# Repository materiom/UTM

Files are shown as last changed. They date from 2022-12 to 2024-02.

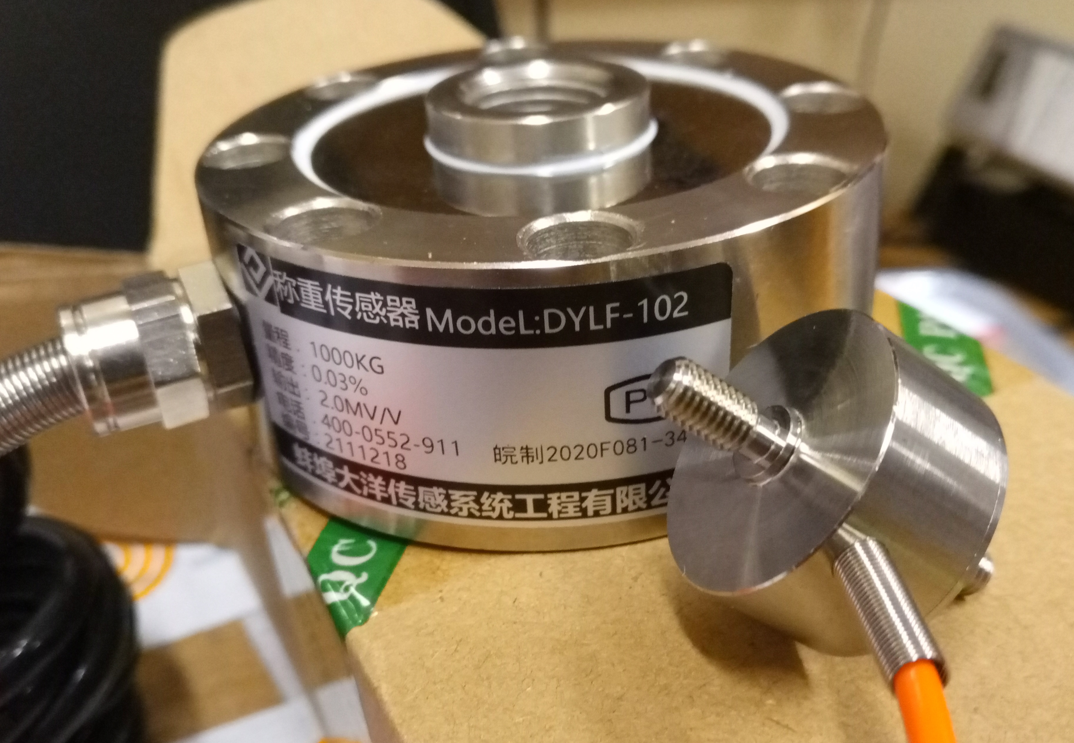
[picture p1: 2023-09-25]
Docs/Doc images/Mechanical - miscellaneous/Load cell photos/Load cell photo.jpg

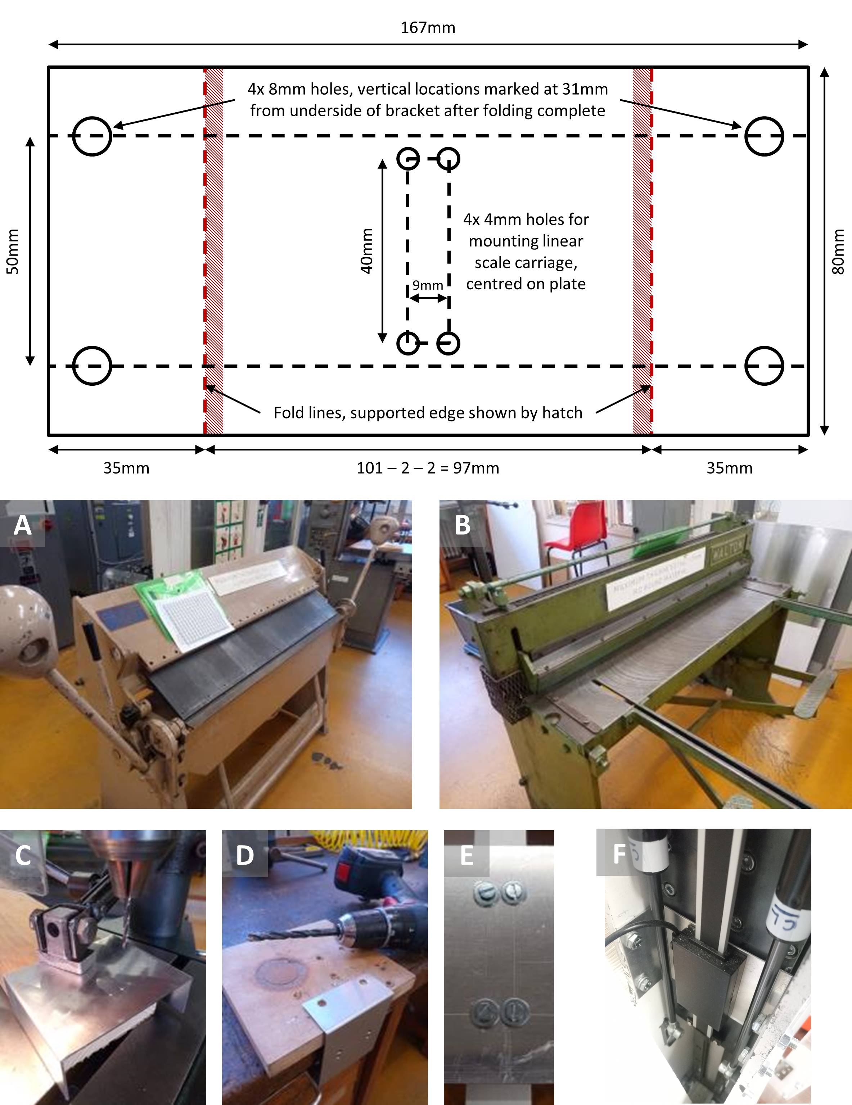
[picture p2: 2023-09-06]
Docs/Doc images/Mechanical - miscellaneous/Linear scale bracket/Linear scale bracket tiled.jpg

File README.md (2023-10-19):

# UTM
Documentation the Materiom Universal Testing Machine

[<b>Read the Documentation - Wiki</span></b>](../../wiki) 

## Introduction

Why do I want to build a UTM?

What solutions are out there (Link to Dave and Richards combined document)

Why another UTM? Why ours?

What problem(s) does it solve?

What is the overall aim for the UTM project

Describe the components
  - Control System / Software - Schematic of how the components all work together
  - User Interface (GUI) - ...
  - Integration with Materiom's database (if this matches with Materiom's goals?)

## Documentation

Description of what is in the documentation and an overview of the structure - add links to the docs here
  
  - Bill of Materials - Items, Quantities, Suggested suppliers, (estimated costs?)
  - CAD files - DXF files, FreeCAD assemblies, CAD library

  - Software use instructions 

## Contribution Guidelines

How can the community contribute to this project?

How can they feedback problems/improvements to make the UTM an ever-improving machine.

Folders in the repo for expansion module information - environmental chamber, heat chamber ideas etc.

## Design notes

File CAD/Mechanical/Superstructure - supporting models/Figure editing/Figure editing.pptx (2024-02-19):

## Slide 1

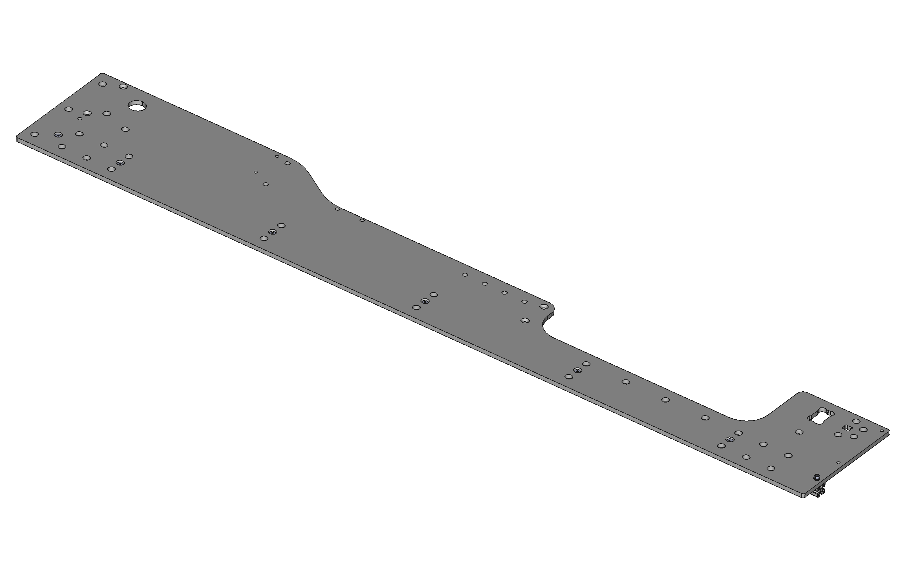
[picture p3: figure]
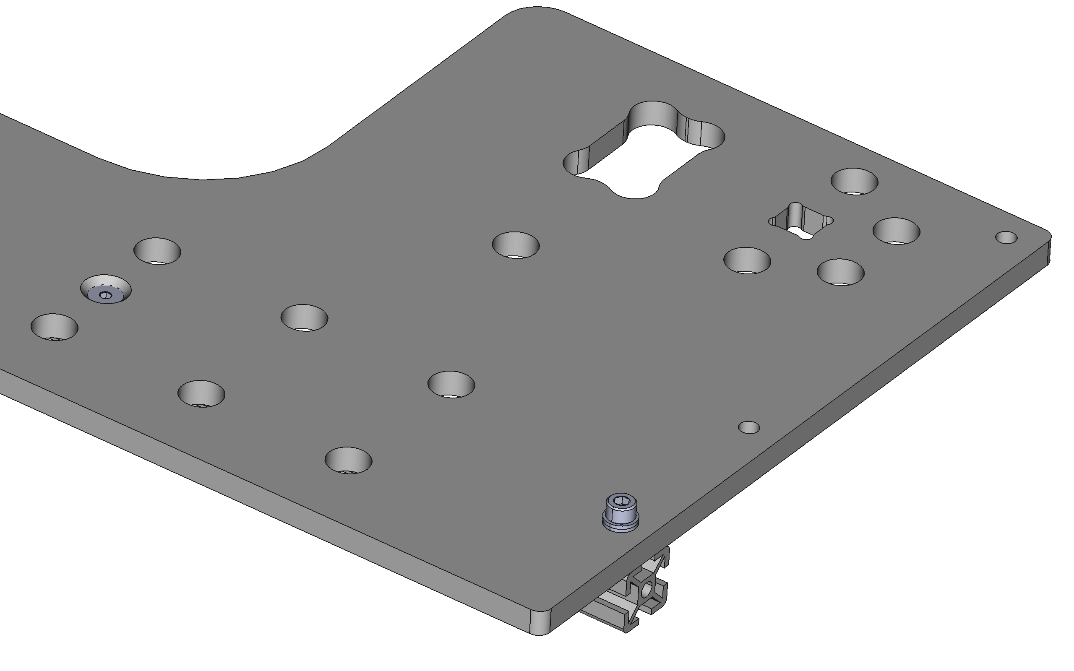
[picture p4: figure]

Rail end aligned with plate end

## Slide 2

Mount centring ring with 2x M4x16mm countersunk head screws

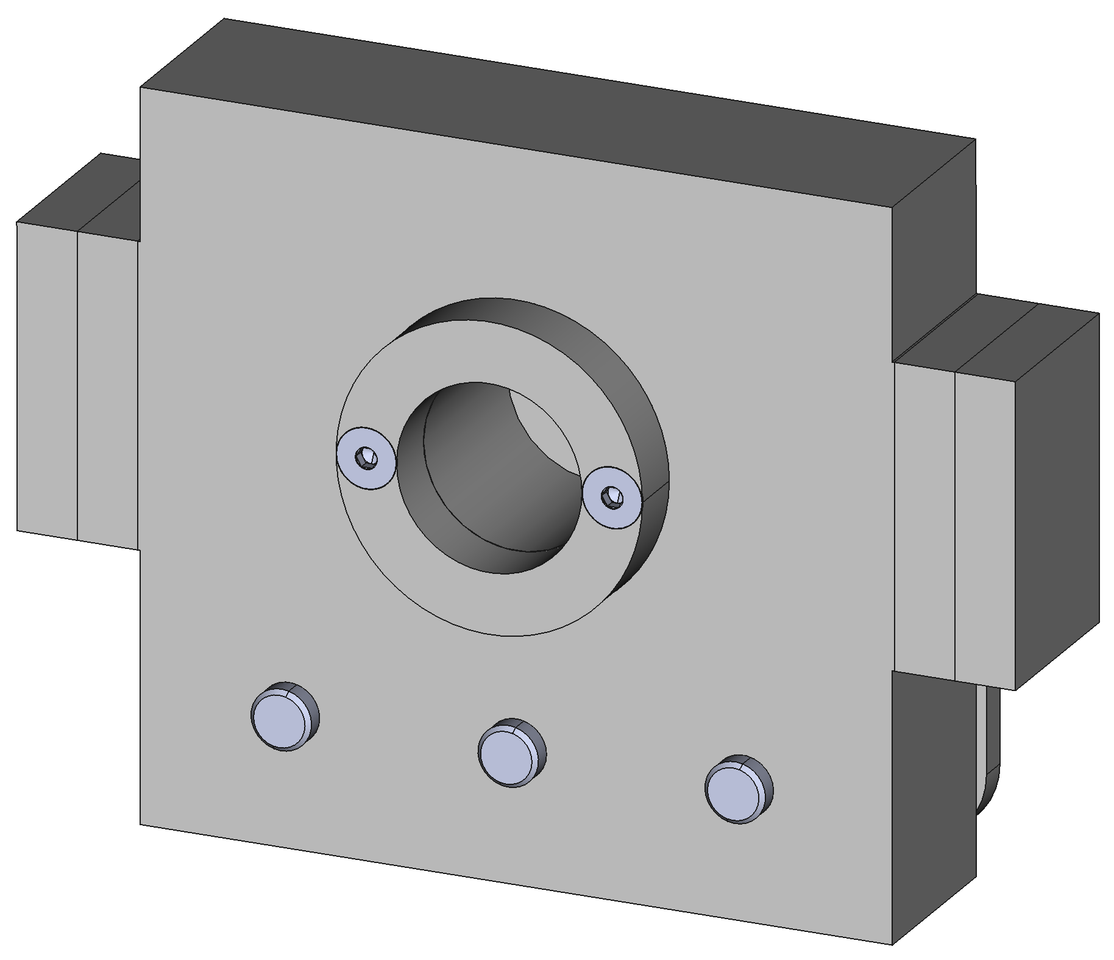
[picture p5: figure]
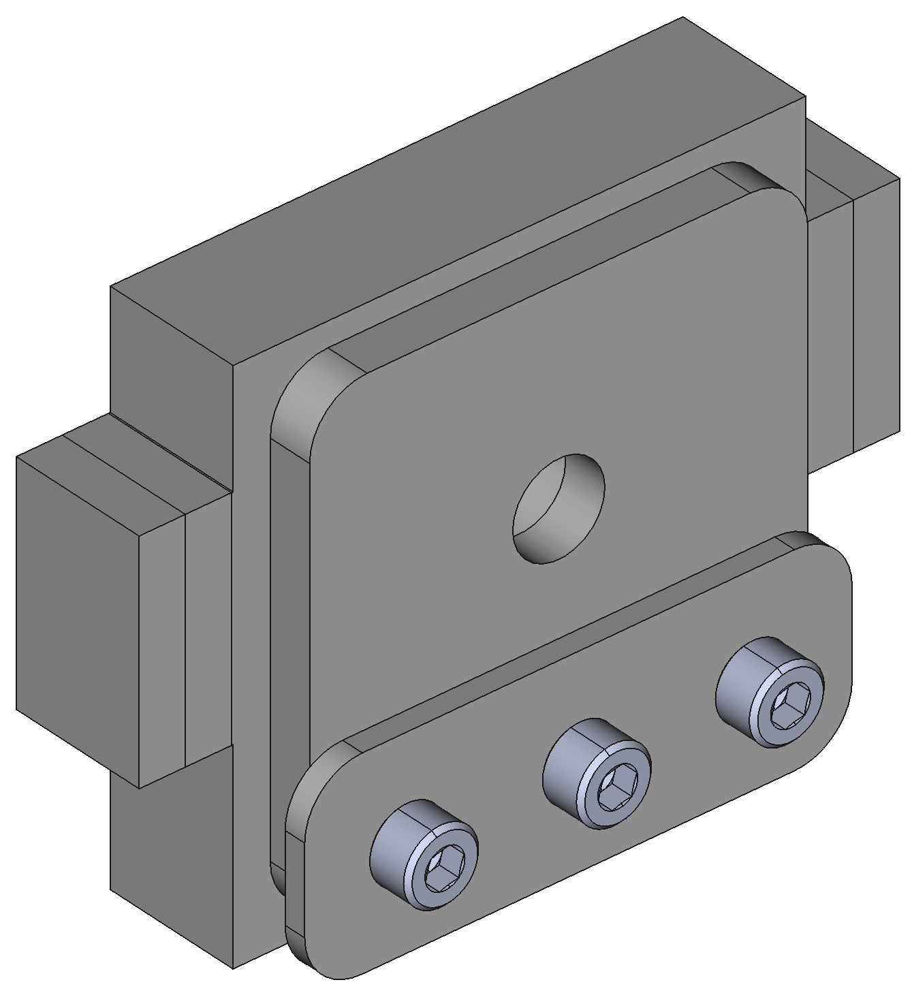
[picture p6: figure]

Mount alignment and associated cap plate with 3x M8x40mm cap head screws

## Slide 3

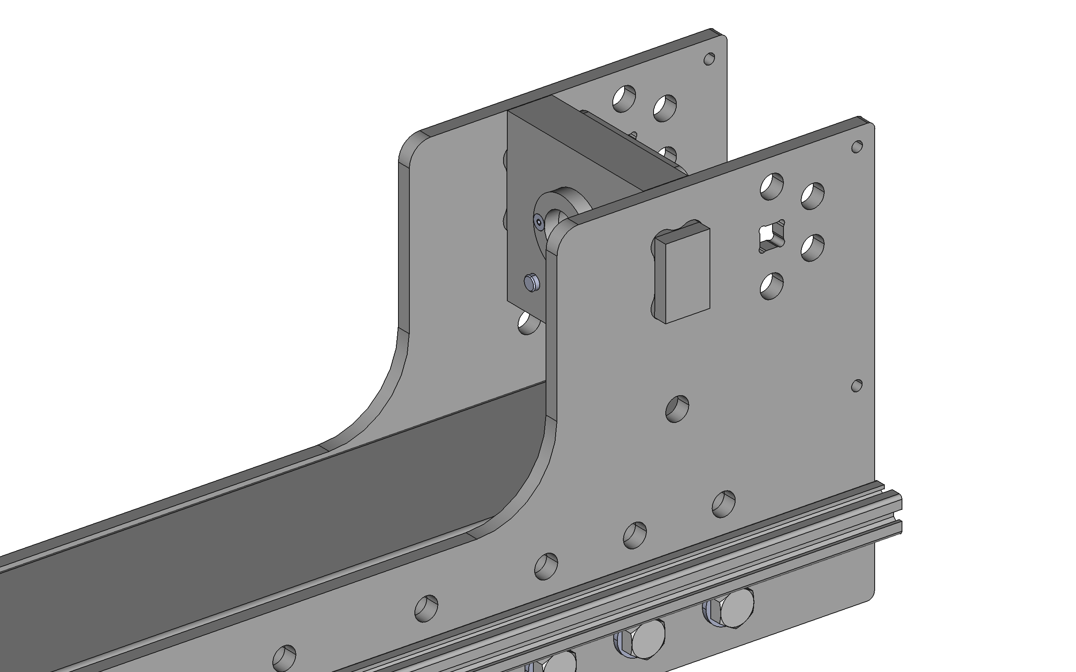
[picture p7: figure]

2. Cut and insert steel shims as necessary to correct alignment of tabbed end plate

1. Check perpendicularity of inside edge of tabbed end plate to instrument side panels

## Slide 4

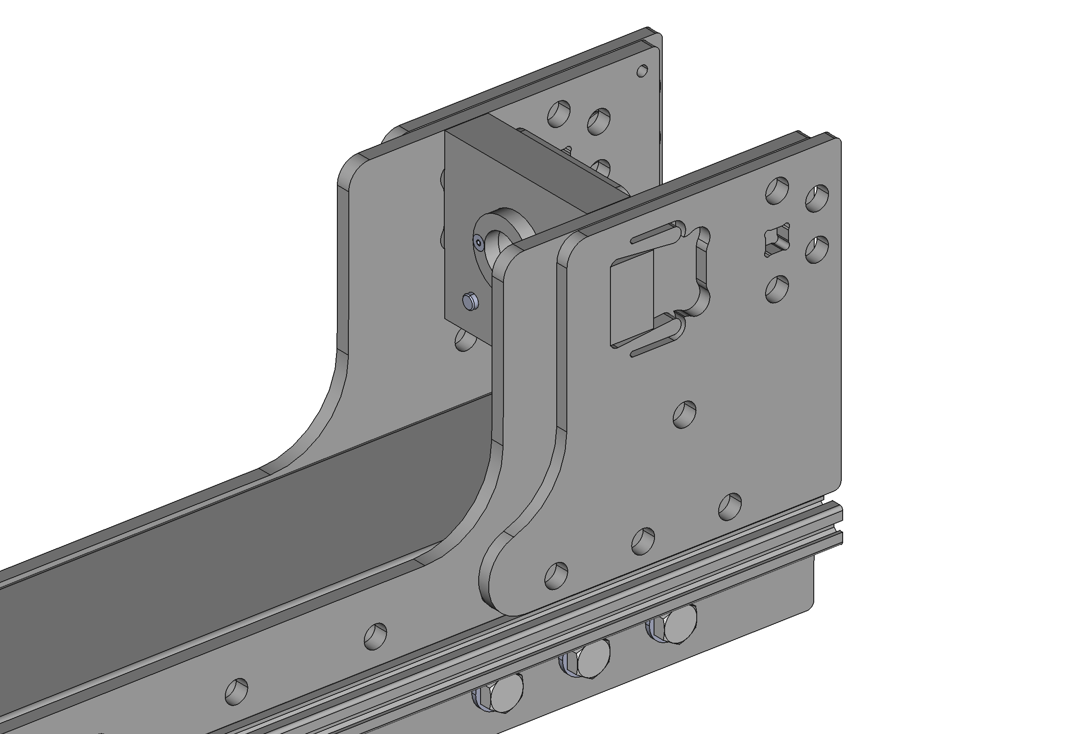
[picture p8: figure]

Drive opposing plates into position with a hammer (ensure steel shims remain in place)

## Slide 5

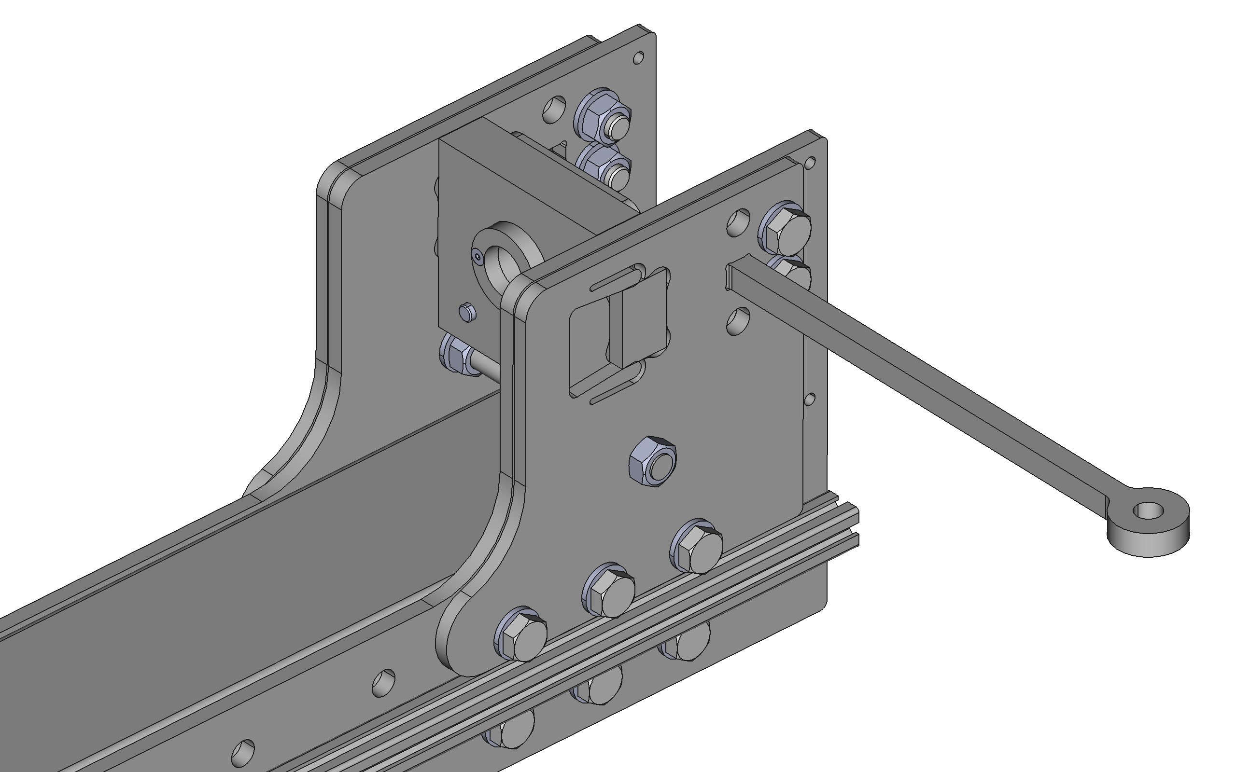
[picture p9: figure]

2. Determine and insert steel shims to permit proper trapping of tabbed end plate
3. Trap by tightening end nuts of installed stud

4. Use the “installation preload tool” to force opposing plate against tabbed end plate whilst initially tightening bolts, repeat for both plates

1. Loosely install additional bolts and stud for this step

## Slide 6

Mount rails with 28x M5x25mm cap head screw

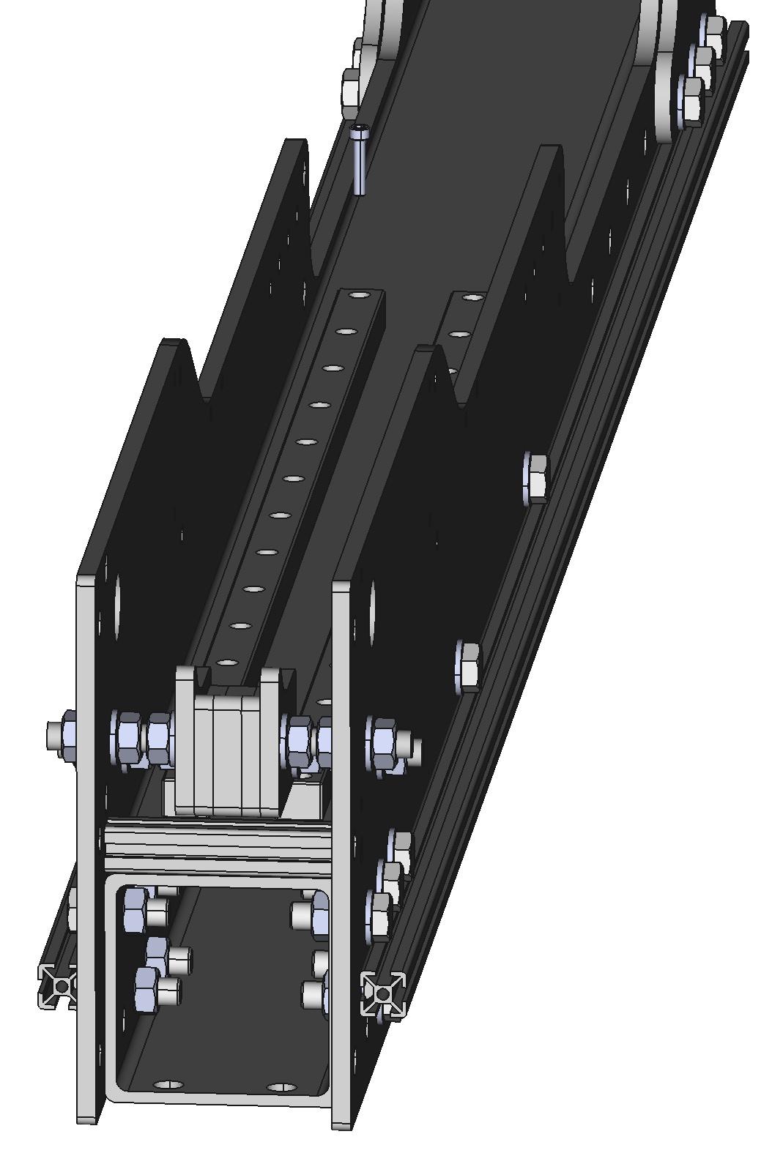
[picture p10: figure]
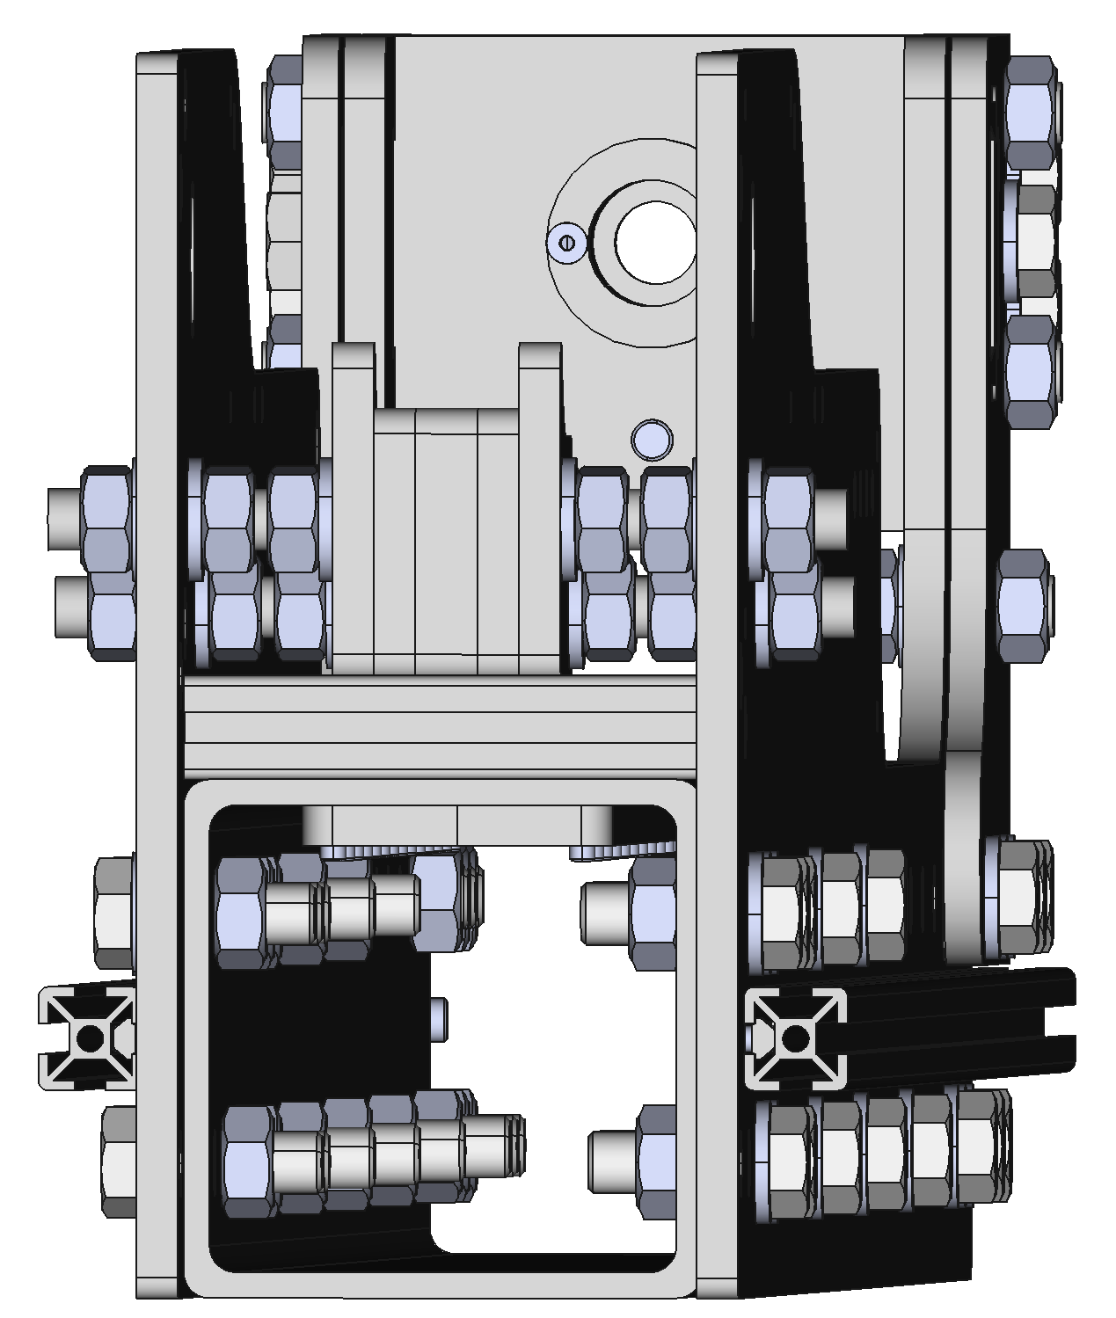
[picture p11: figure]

Tapped plate

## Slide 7

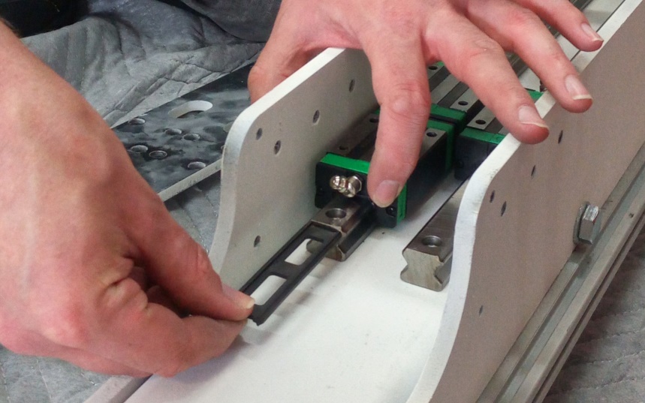
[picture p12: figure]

Detail of setting first rail parallel to instrument frame using a dial test indicator

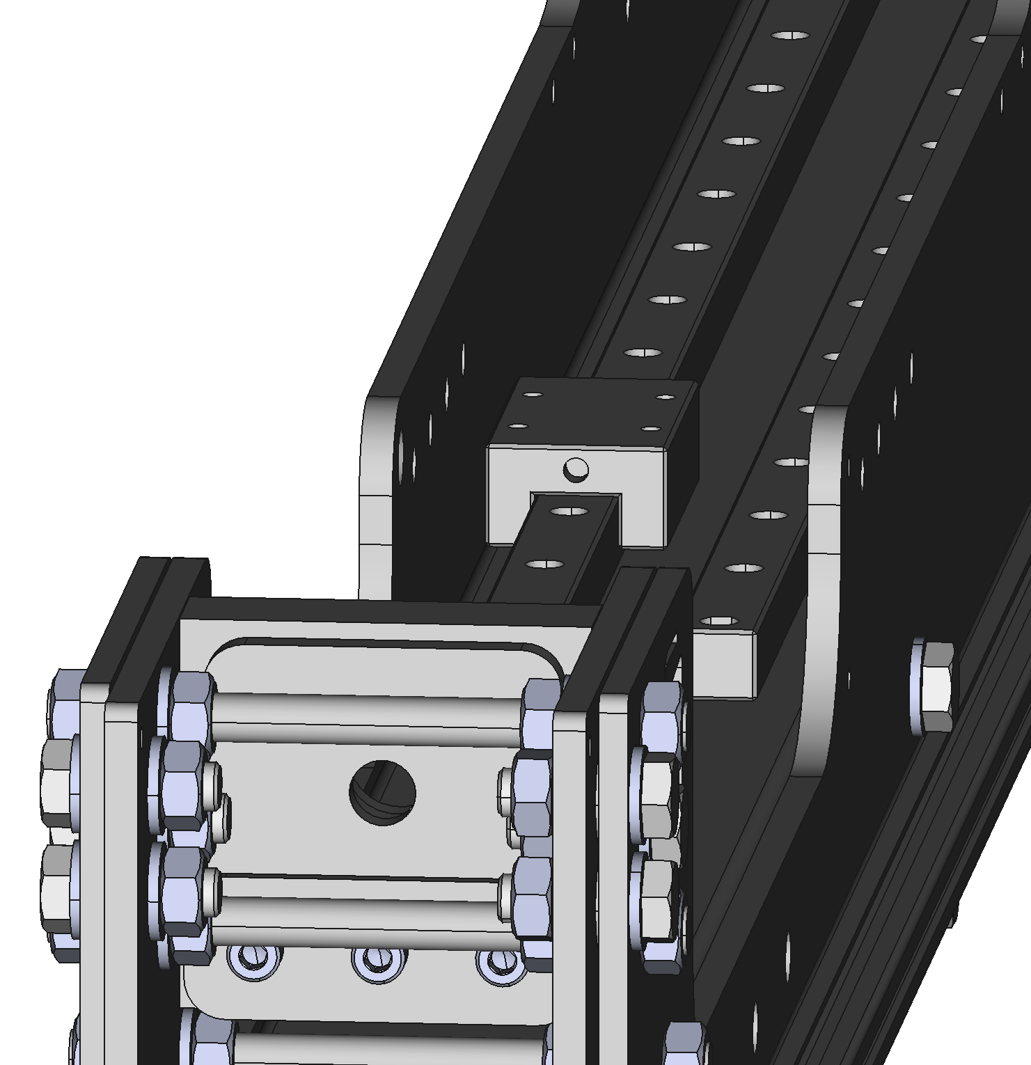
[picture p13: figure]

Detail of setting second rail parallel to first rail using a dial test indicator

Slide ball bearing carriage from insert onto rail

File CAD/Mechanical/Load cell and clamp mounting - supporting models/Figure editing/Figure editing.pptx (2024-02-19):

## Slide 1

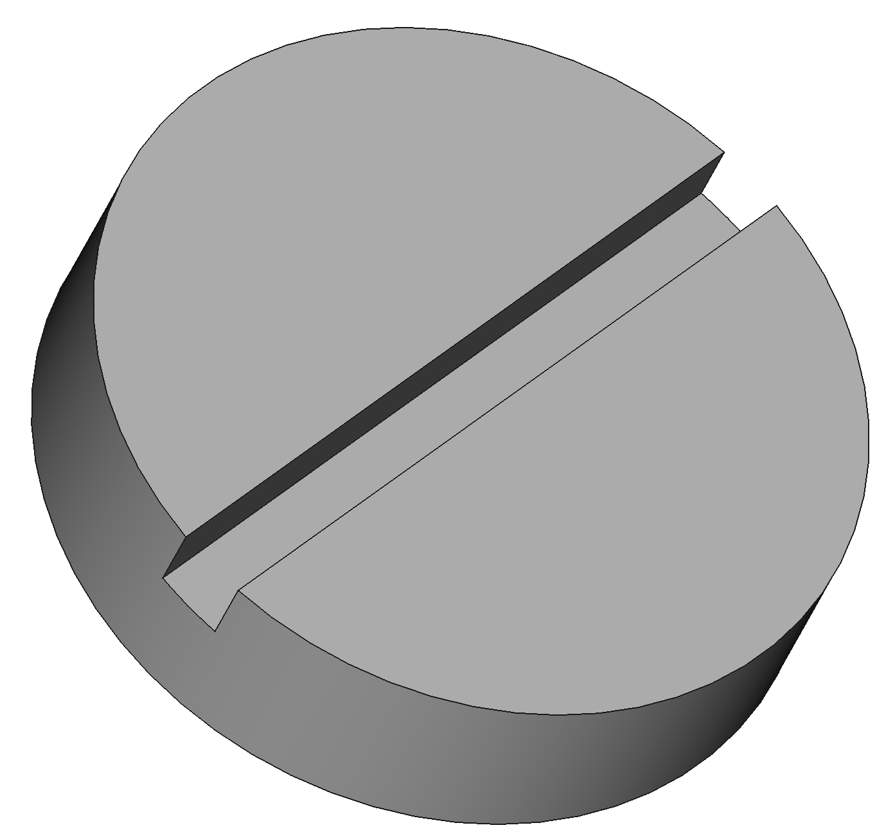
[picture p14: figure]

Fit plugs flush to surface and lightly thread lock into place

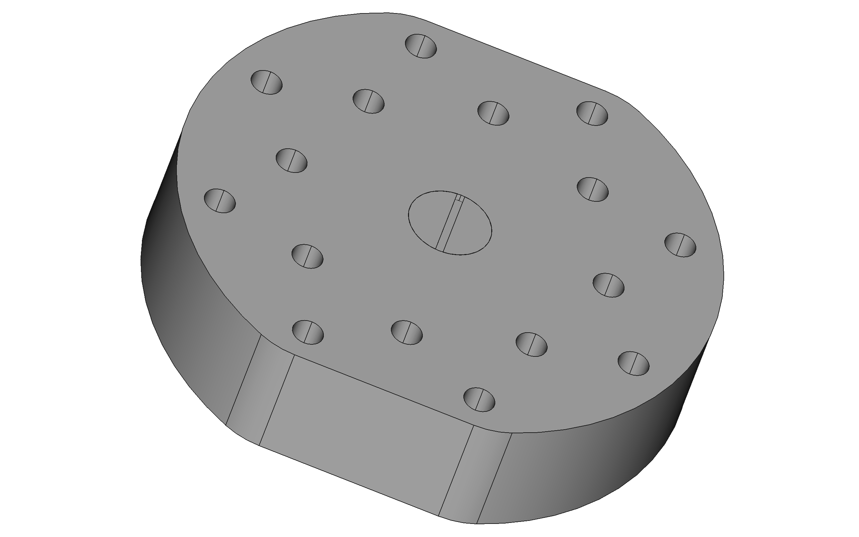
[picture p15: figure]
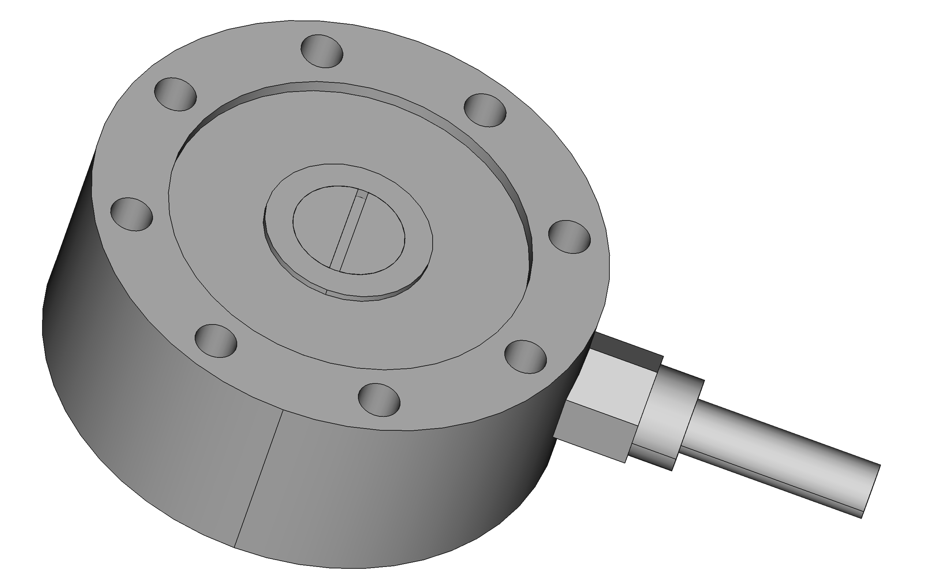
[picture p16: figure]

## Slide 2

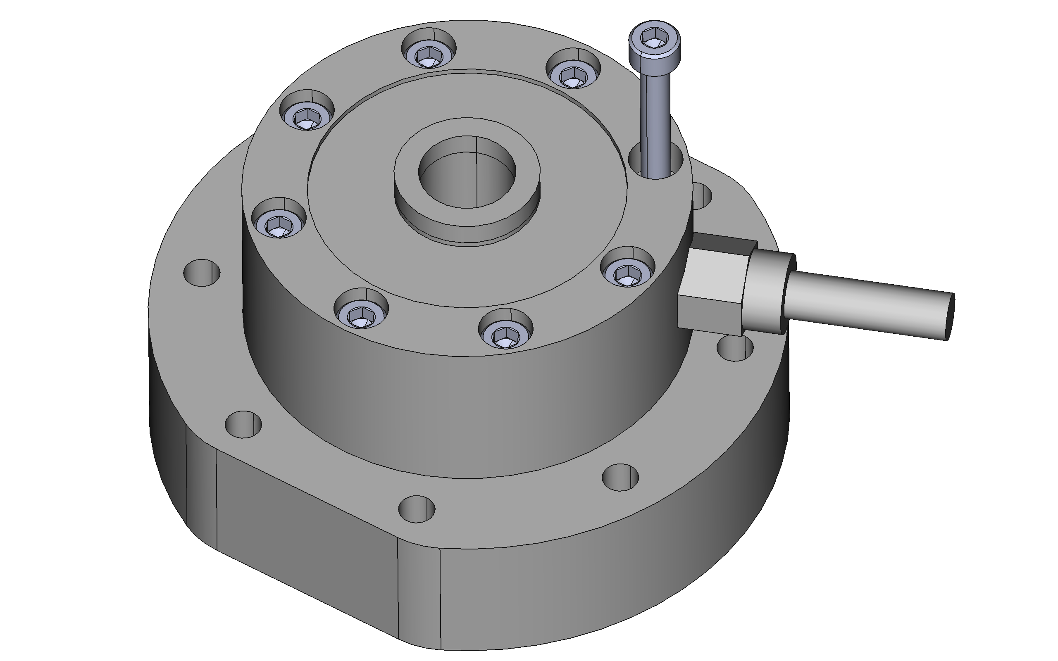
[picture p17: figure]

Mount with 8x
M5x45mm cap head screw

Plugs should face each other

Orient load cell to direct cable near parallel to straight edges of mounting plate

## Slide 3

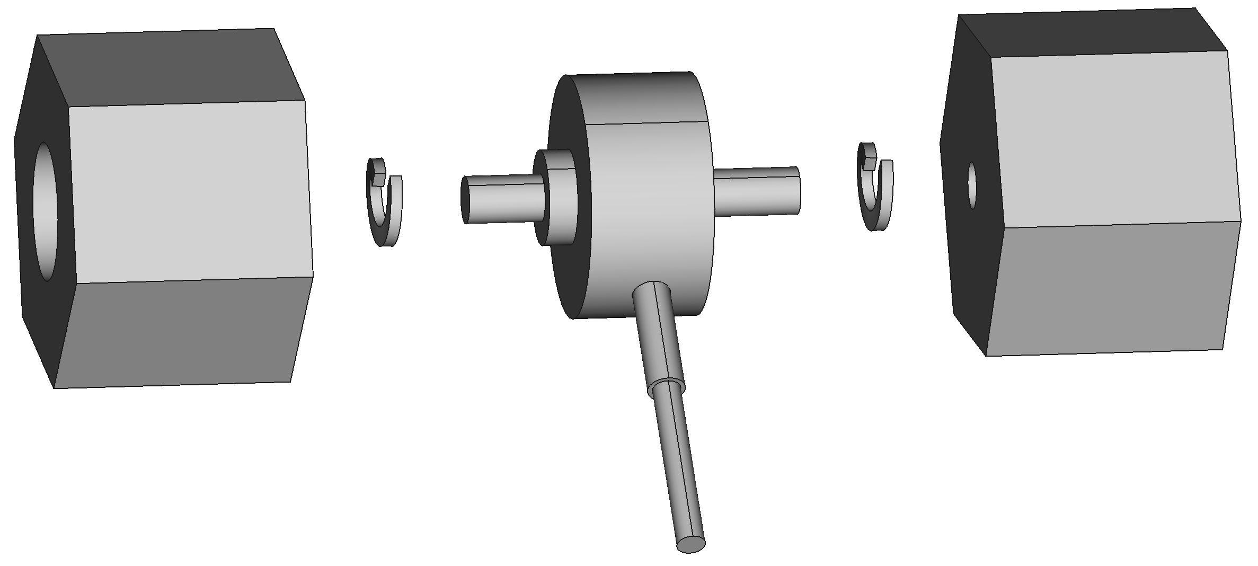
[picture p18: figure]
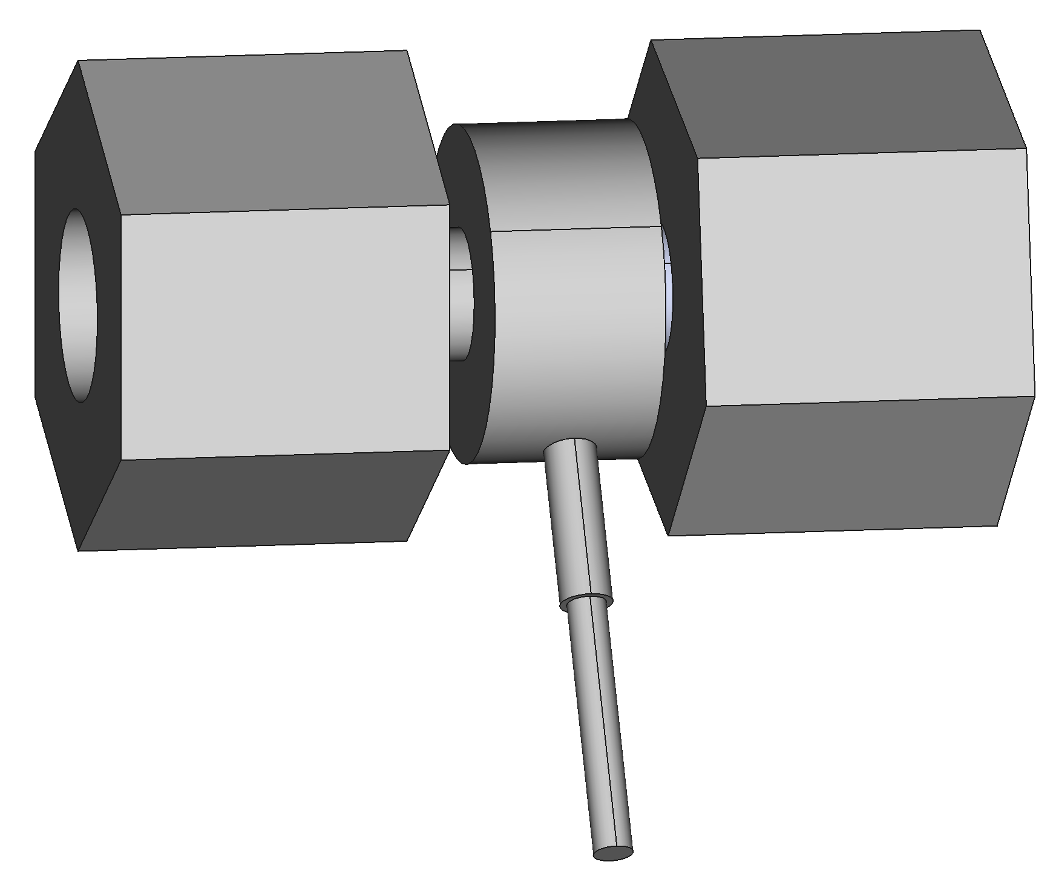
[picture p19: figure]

50kg load cell mounted between two thread adaptors – tighten by hand only. Ideally use shake proof split washers.

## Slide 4

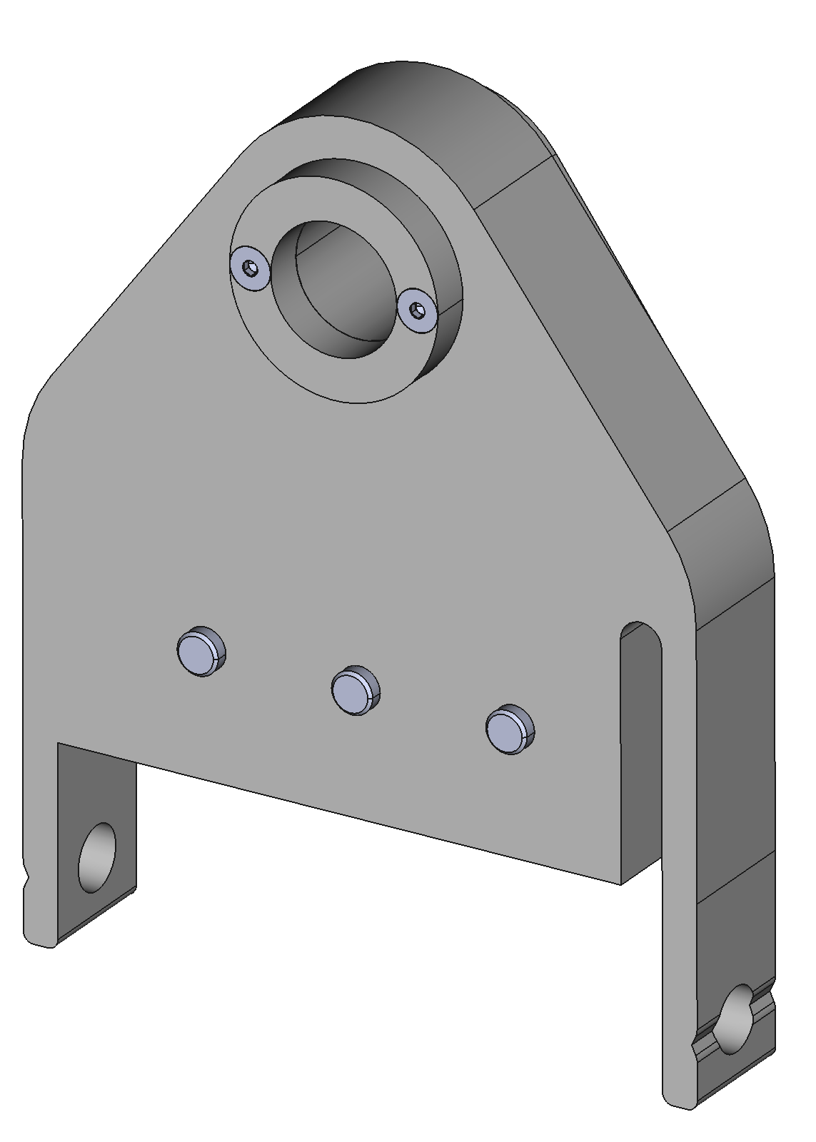
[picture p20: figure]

Mount centring ring with 2x M4x16mm countersunk head screws

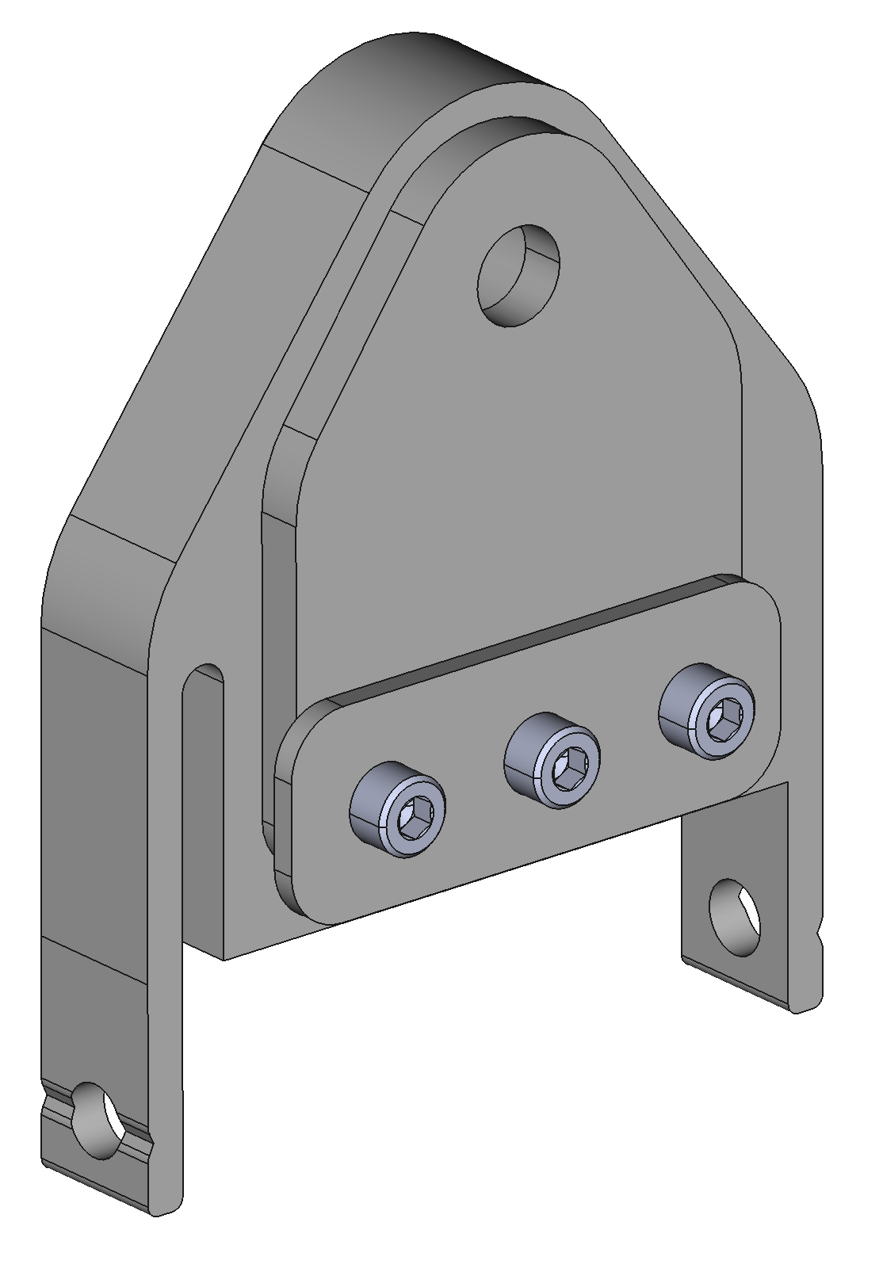
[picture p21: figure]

Mount alignment and associated cap plate with 3x M8x40mm cap head screws

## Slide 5

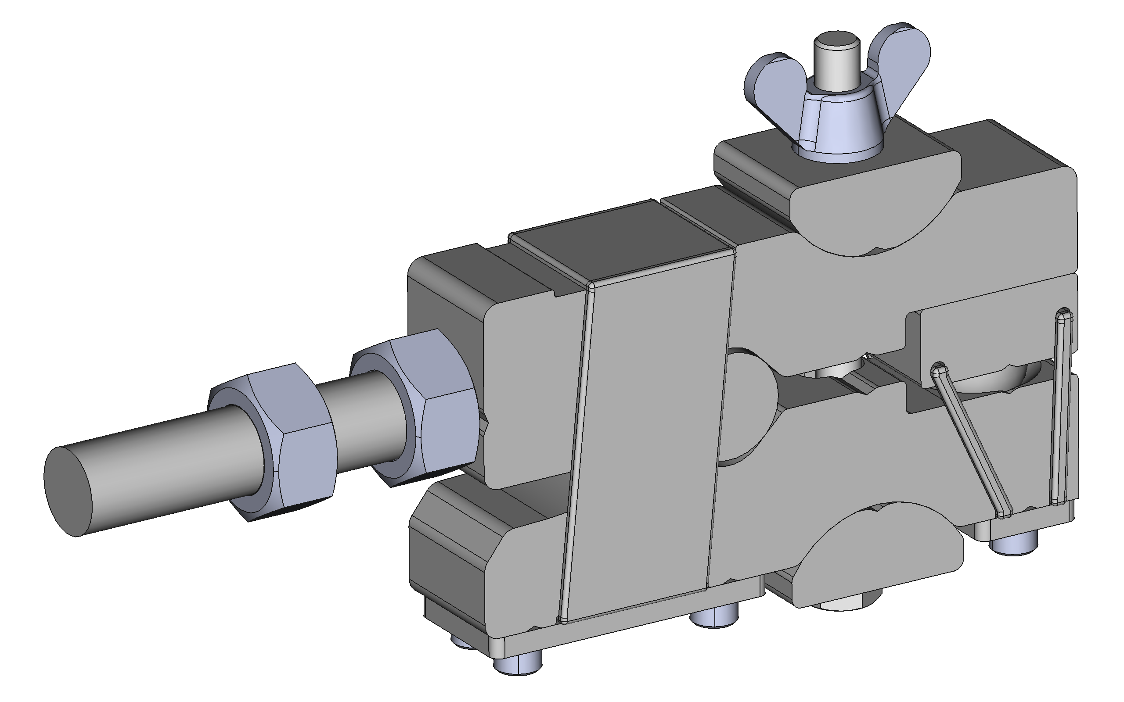
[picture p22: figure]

Closest approach at 160mm travel: stud length ensures clash should not occur with clamp (given clamp orientation shown)

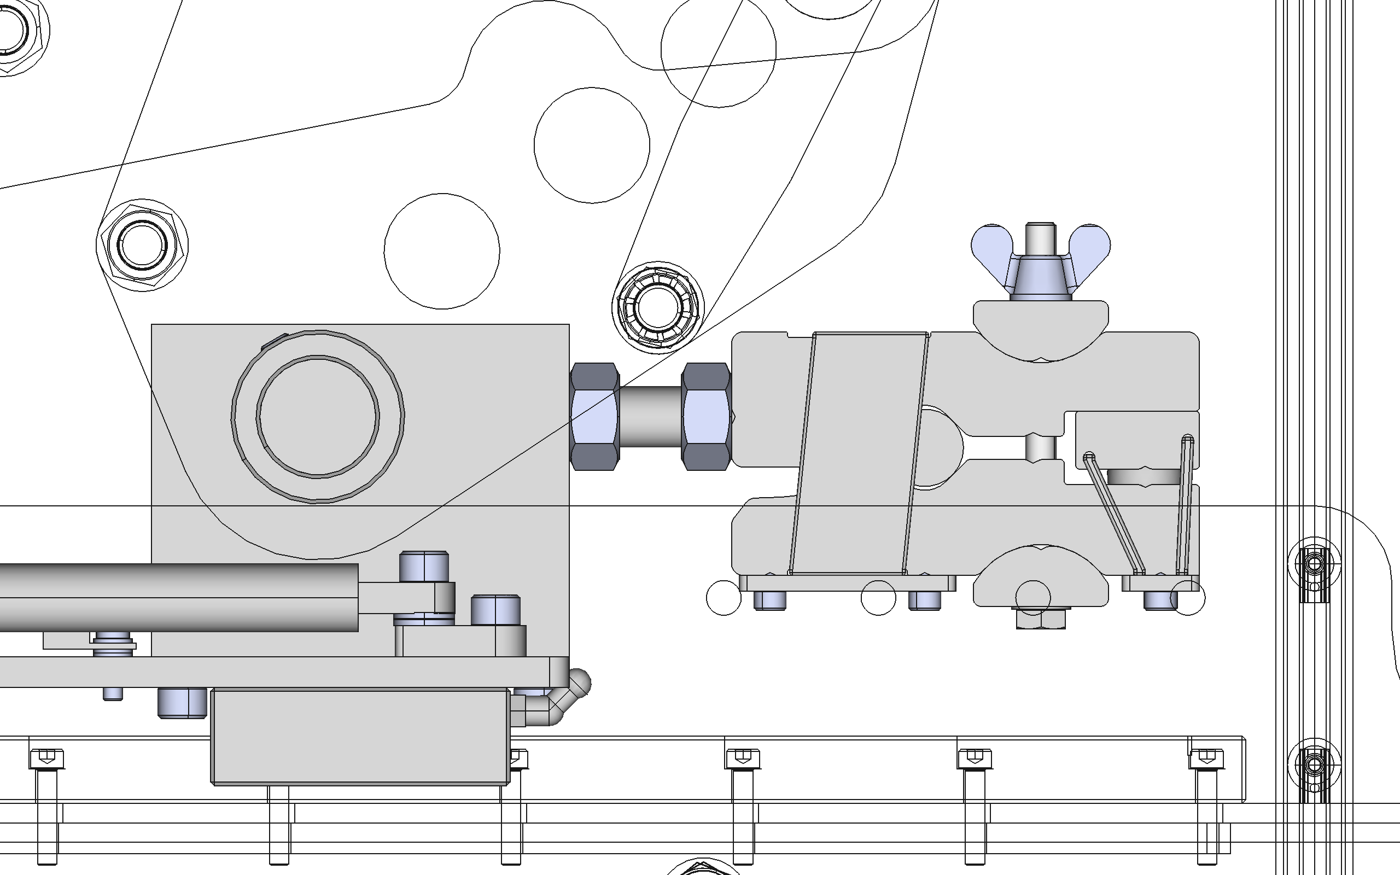
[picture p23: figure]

Stud and right hand nut lightly thread locked into clamp body

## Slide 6

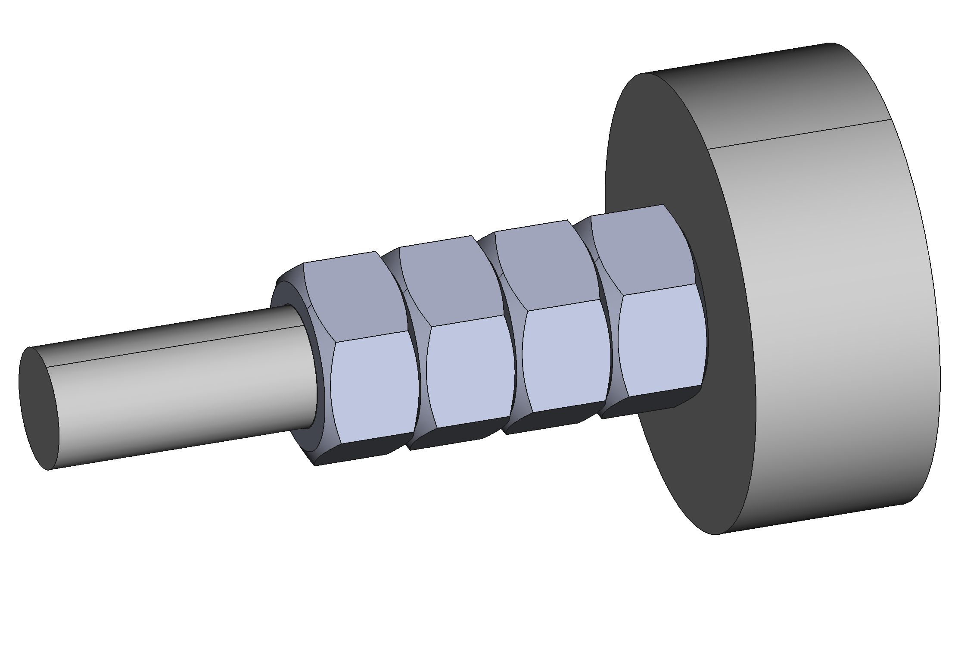
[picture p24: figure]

Stud lightly thread locked into compression plate body and last nut lightly thread locked into place

Stud length and nut stack ensures clash should not occur with compression plate

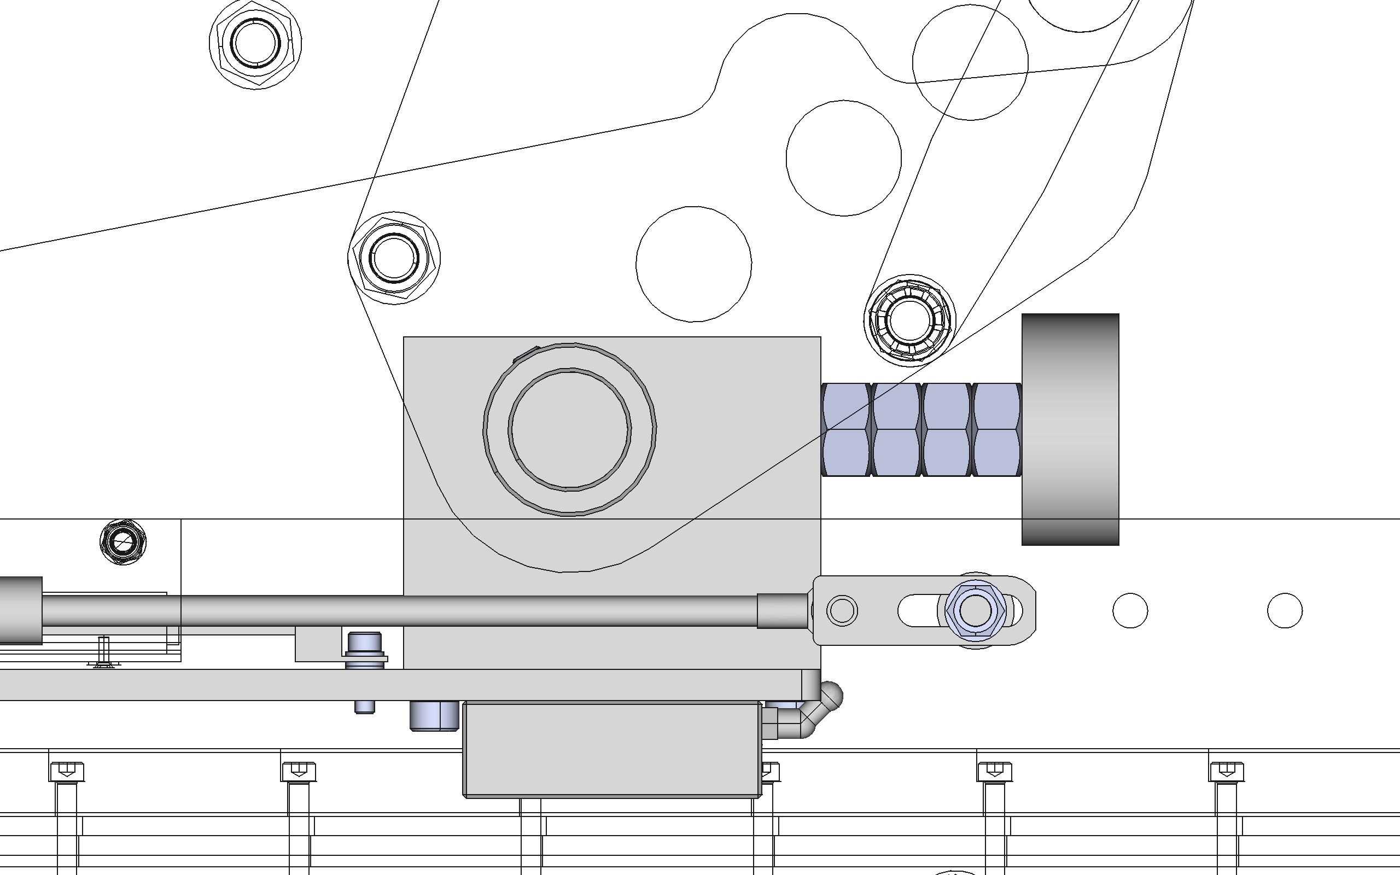
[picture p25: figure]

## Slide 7

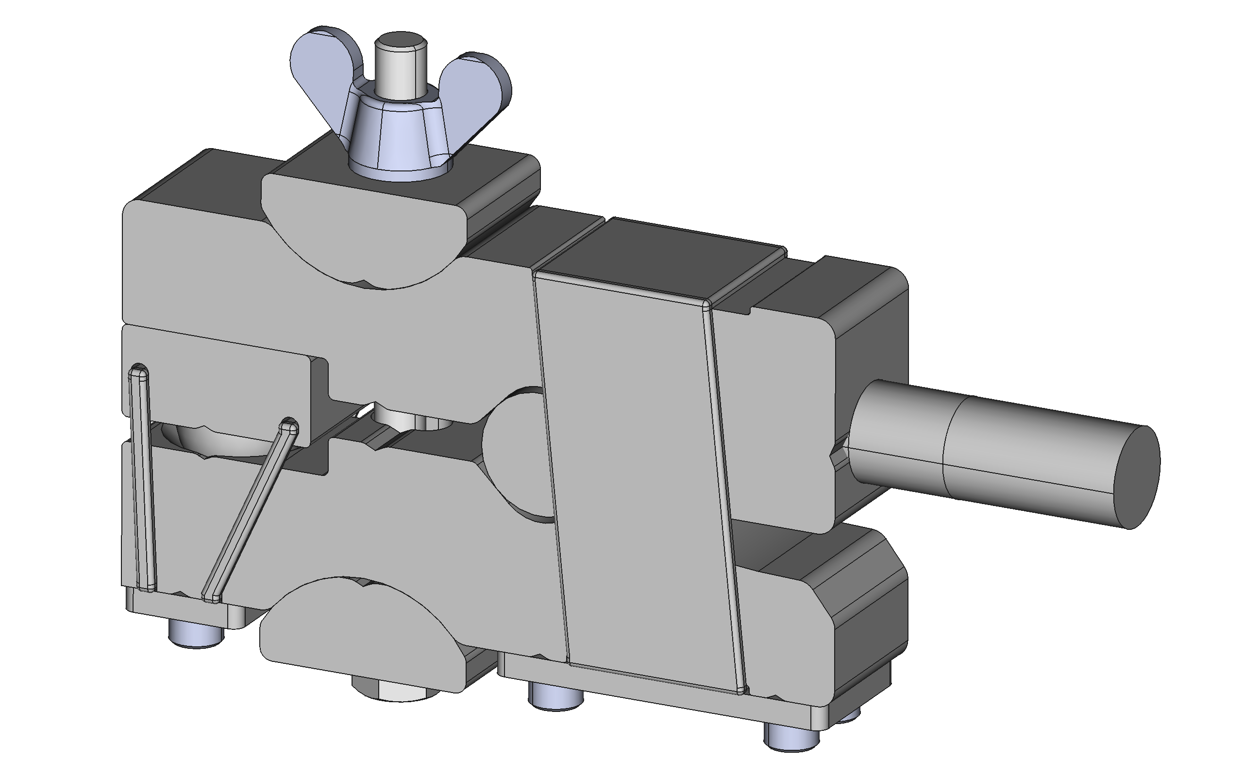
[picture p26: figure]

Stud lightly thread locked into clamp body

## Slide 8


Stud lightly thread locked into compression plate body

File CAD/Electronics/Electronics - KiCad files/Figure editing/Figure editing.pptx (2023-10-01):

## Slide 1

Main PCB exemplar circuit diagram and PCB images


Amplifier PCB exemplar circuit diagram and PCB images


Click image for link to KiCad files


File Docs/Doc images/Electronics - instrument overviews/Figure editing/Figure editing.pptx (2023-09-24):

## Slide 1

24V PSU

DC-DC CV-CC Module

Fuse/
crowbar

LED Light source

L298N Bridge driver

Motor direction

Arduino pro-micro (common 5v variant)

Estop/interlocks

Motor drive

Tacho signal

DC-DC CV-CC Module

DC-DC CV Module

Fuse/
crowbar

LED Light source

Actuator power

Tacho power

Linear actuator

Fuse/
crowbar

Spare analogue pro-micro input

Camera

CSI Camera bus

Linear scale
(currently via Pi Pico)

USB

Motor PWM

Motor current

Interlock signal

Hardware jog control

LED current control

I²C 5v

Pi cooling fan

BSS138 based level shifter

I²C 3.3v

Raspberry Pi 4
(GPIO brought out to pass-through connector: all pins used are via cuttable jumpers)

User interface and instrument control (monitor/
keyboard/
mouse)

DC-DC CV Module

5v digital power

Fuse/
crowbar

GPIO 5v

5v power to Pi

GPIO 3.3v

External load cell amplifier enclosure

5V Linear regulator

5V analogue power

Footprint for NAU7802

Digital power

Spare data bussses

3.3v power from
Pi (on-board regulator)

SPI 3.3v

Load cell input A

Signal key
24v Input power
5v Digital power
3.3v Digital power
5v Analogue power
General signal
Data bus
Drive power path

Load cell input B

Footprint for HX711

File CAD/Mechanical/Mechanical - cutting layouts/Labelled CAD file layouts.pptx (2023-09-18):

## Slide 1


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
4-10

4-5

4-4

4-13

4-5

4-1

4-1

4-10

4-14

4-11

4-12

4-13

4-14

4-11

4-8

4-8

4-8

4-8

4-1

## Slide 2

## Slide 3


8-3

8-2 x2

8-8 x10

8-16

8-19

8-12

8-5 x2

8-11 x2

8-2 x2

8-3

8-7

8-6 x2

8-1 x4

8-12

8-7

8-19

8-14

8-17

8-9

8-14

8-21

8-20

8-20

8-10

8-15 x2

8-13 x2

8-18

8-21

8-4

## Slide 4

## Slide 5


12-7 x2

12-2 x2

12-6

12-3 x5

12-5

12-1

12-1

12-4

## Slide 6

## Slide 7


25-8

25-3

25-3

25-2

25-9

25-2

25-8

25-3

25-5

25-3

25-7

25-6

25-8

25-2

25-2

25-8

25-4

25-5

25-8

25-8

25-1

25-8

25-8

25-4

25-1

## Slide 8

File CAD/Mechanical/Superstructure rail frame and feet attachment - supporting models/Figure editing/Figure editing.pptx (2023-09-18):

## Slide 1


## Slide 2


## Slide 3


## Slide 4


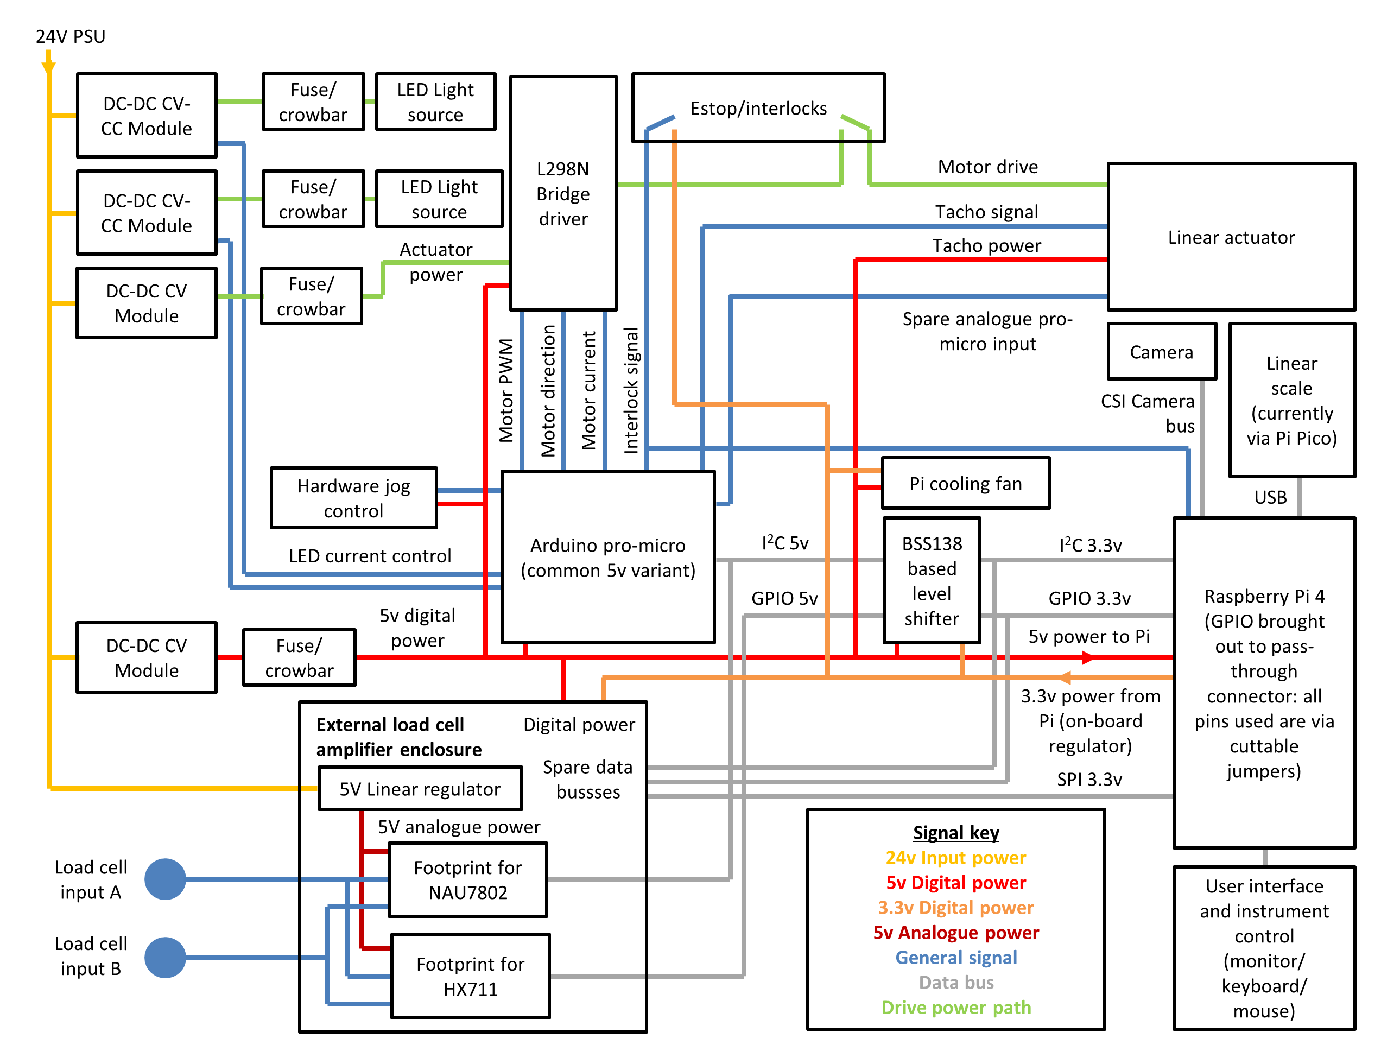
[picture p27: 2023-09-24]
Docs/Doc images/Electronics - instrument overviews/Instrument electronics overview.png

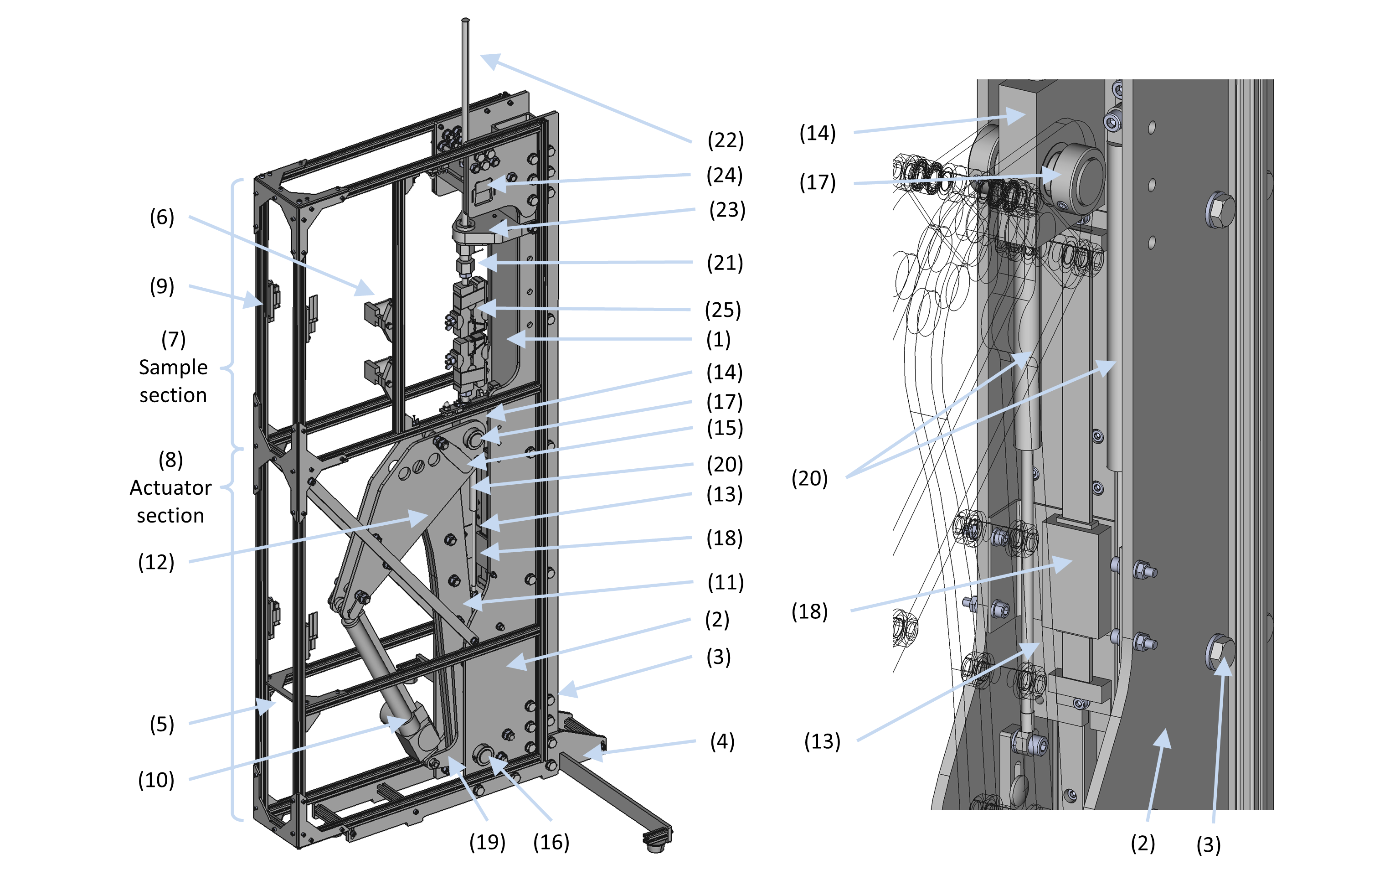
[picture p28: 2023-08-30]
Docs/Doc images/Mechanical - instrument overviews/Instrument mechanical overview.png

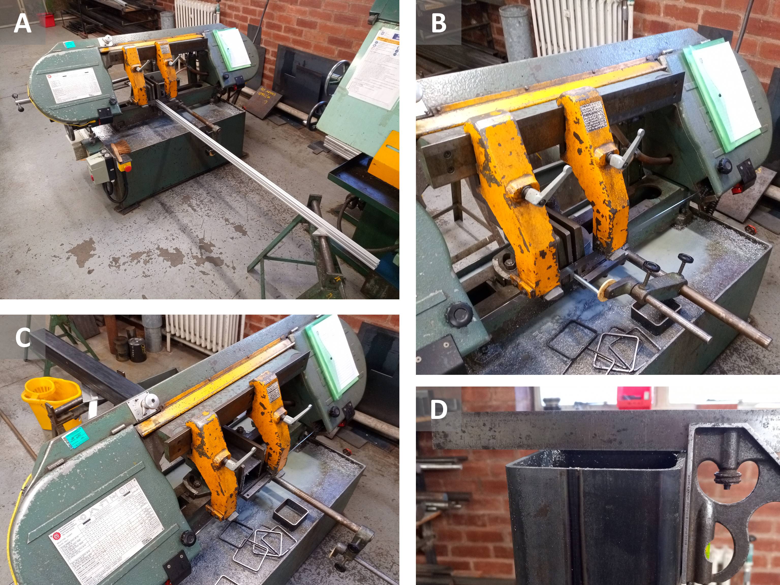
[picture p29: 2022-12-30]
Docs/Doc images/Mechanical - miscellaneous/Bandsawing/Bandsawing photos tiled.jpg

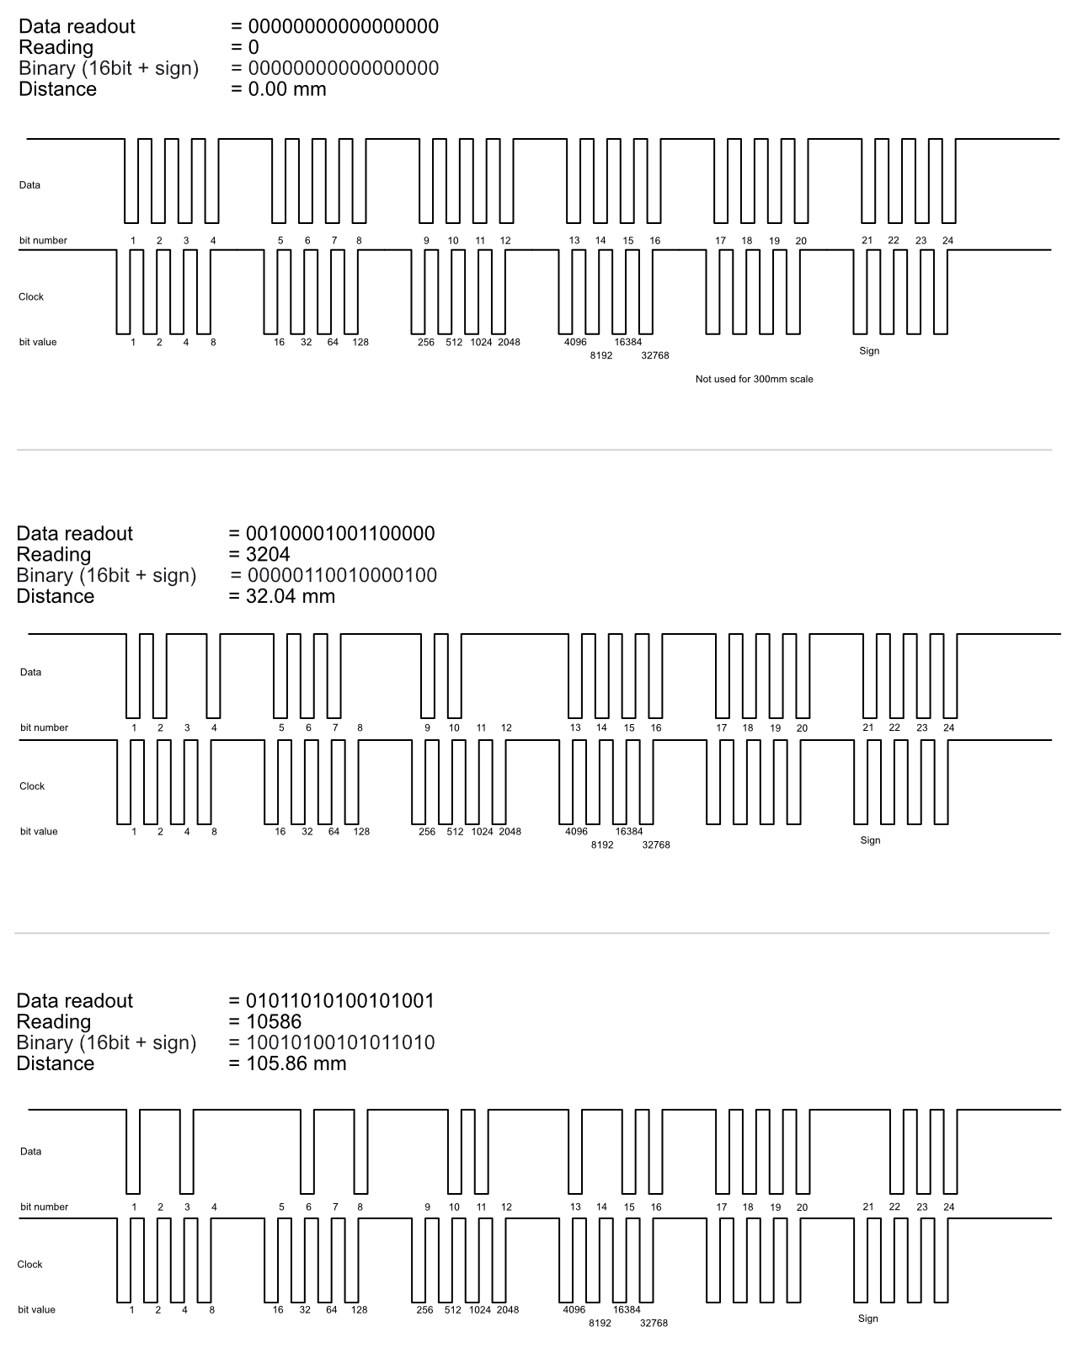
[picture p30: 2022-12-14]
Docs/Doc images/Electronics - digital scale implementation/DRO Digital Protocol Readout.png

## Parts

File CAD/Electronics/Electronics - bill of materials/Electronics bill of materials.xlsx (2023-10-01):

Description / section | Quantity | Supplier | Part number | Notes
See mechanical bill of materials for: linear actuator, electronics mounting hardware/cable management, linear scale and load cells
IF LINE HIGHLIGHTED ORANGE - ORIGNAL LISTING NO LONGER EXISTS. CLOSEST PART LINKED TO / IMAGE PROVIDED FOR REFERENCE
Raspberry Pi / Arduino related hardware
Pro Micro - 5V/16MHz | 1 | https://shop.pimoroni.com/ | DEV-12640
Raspberry Pi Camera Cable (100cm) | 1 | https://shop.pimoroni.com/ | CAB0304
2x20 pin Female GPIO Header for Raspberry Pi | 1 | https://shop.pimoroni.com/ | COM0002 | Main GPIO connection
Raspberry Pi High Quality Camera | 1 | https://shop.pimoroni.com/ | RPI-073
Lens for the Raspberry Pi High Quality Camera | 1 | https://shop.pimoroni.com/ | RPI-074
Raspberry Pi 4 Essentials Kit | 1 | https://shop.pimoroni.com/ | PIM620 | Raspberry Pi 4 with SD card, video lead etc
114992160 - ICE Tower Cooler for Raspberry Pi | 1 | CPC/Onecall | SC15644
MCDTS6-5K Switch, Tactile 9.5mm 100g | 1 | CPC/Onecall | SW02470 | Arduino reset button
BOB-12009 - Bidirectional Logic Level Converter Board | 1 | CPC/Onecall | MK00748
2213S-40G 2.54mm Pin Header, 2 Row, 40 Way, Vertical | 5 | CPC/Onecall | CN21891 | GPIO pass through + general jumpers
2214S-40SG-85 PCB Receptacle, Board-to-Board, 2.54 mm, 2 Rows, 40 Contacts, Through Hole Mount | 1 | Farnell/Onecall | 2847248 | GPIO breakout
General parts
MCFYU6104Z6 Ceramic Disc Capacitor, 0.1 µF, 50 VDC, 5 mm | 2 (x10) | CPC/Onecall | CA05016
K/RES-E12 Resistor Set, Cf, 1/4W, 5%, E12, 610 Pieces | 1 | CPC/Onecall | RE07593 | General purpose kit
P160KNP-0QC20B10K Rotary Potentiometer, Conductive Plastic, 10 kohm, 1 Turns, Linear, 200 mW, ± 20%, P160 | 1 | Farnell/Onecall | 1760793 | Jog potentiometer (development)
MPGCS-014-SM4-30G THERMAL SILICONE GREASE, 30G, WHITE | 1 | Farnell/Onecall | 3267499 | For L298N heatsink - any suitable compound could be used
MC34743 Pin Header, Board-to-Board, 2.54 mm, 1 Rows, 24 Contacts, Through Hole, MC34 | 10 (MOQ) | Farnell/Onecall | 1593425 | Single row pins for e.g. Arduino / level shifter mounting
30cm 3 Pin PC Fan Male Plug to Female Socket Power Extension Cable [006341] | 1 | Ebay | https://www.ebay.co.uk/itm/383662021066 | Jog pot extension cable and provides PCB header socket
Power related, setup and crowbar circuits
15DYS6150-2400625P - 24V, 6.25A, 150W, Desktop Power Supply (Level VI), IEC C14, 2.1mm Plug | 1 | CPC/Onecall | PW04202
PE01062 1m UK Plug to IEC C13 Socket Mains Lead, Black | 1 | CPC/Onecall | PL13309
FC68148 - DC Power Socket, PCB Mount, DC 10A | 1 | CPC/Onecall | CN01545
LMV431AIZ/NOPB - Voltage Reference, Precision, Shunt - Adjustable, LMV431A Series, 1.24V to 30V, TO-226AA-3 | 4 | Farnell/Onecall | 3009285
MC-2228BG 2.54mm Shorting Link, Closed, Black | 10 | CPC/Onecall | CN21839 | "Jumpers"
MC33163 Resettable Fuse, PPTC, MC33, 30 VDC, 3 A, 6 A, 10.8 s, Rectangular | 4 | Farnell/Onecall | 1800719
BTB12-600TW3G Triac, 600 V, 12 A, TO-220AB, 5 mA, 1.3 V, 20 W | 4 | Farnell/Onecall | 2777137
D103K43Y5PH6TJ5R Ceramic Disc Capacitor, 10000 pF, 100 V, ± 10%, Y5P, 5 mm, Radial Leaded | 10 (MOQ) | CPC/Onecall | CA07980
Through Hole Resistor, 43 kohm, MF25, 250 mW, ± 1%, Axial Leaded, 250 V | 10 (MOQ) | Farnell/Onecall | 9341919
MF25 13K Through Hole Resistor, 13 kohm, MF25, 250 mW, ± 1%, Axial Leaded, 250 V | 10 (MOQ) | Farnell/Onecall | 9341285
3296W-1-503LF Trimmer, 25 Turn 50K | 3 | CPC/Onecall | RE06697
MCL053GD LED, Green, 5mm, 2.1V | 10 (MOQ) | CPC/Onecall | SC15414
EEUFM0J222L Electrolytic Capacitor, 2200 µF, 6.3 V, ± 20%, Radial Leaded, 5000 hours @ 105°C, Polar | 1 | Farnell/Onecall | 1219449
5A DC-DC Voltage Step Down Buck Converter Adjustable XL4015 +Heatsink _UK Fast | 2 | Ebay | https://www.ebay.co.uk/itm/154322543465
Load cell amplifier specific
MC-254-30-00-RA-DIP Pin Header, Wire-to-Board, 2.54 mm, 2 Rows, 30 Contacts, Through Hole Right Angle, MC 254 | 5 (MOQ) | Farnell/Onecall | 2843549
FM6725 - DIN Audio / Video Connector, 5 Contacts, Jack, PCB Mount, Solder, Tin Plated Contacts | 2 | Farnell/Onecall | 2679726
590-0500 5 Pin (180 Degree) Nickel Locking DIN Plug | 2 | CPC/Onecall | CN00044 | For load cells
MC003556 Die Cast Aluminium Enclosure, 44.5x82.5x110mm | 1 | CPC/Onecall | EN85551
FC30600-S - Ribbon Cable, IDC Receptacle to IDC Receptacle, 30 Ways, 23.622 ", 600 mm, 2.54 mm | 1 (opt.) | Farnell/Onecall | 2217687 | Longer optional ribbon cable
FC30300-0 Ribbon Cable, IDC Receptacle to IDC Receptacle, 30 Ways, 11.811 ", 300 mm, 2.54 mm | 1 | Farnell/Onecall | 2217629
RXEF005 Resettable Fuse, PPTC, PolySwitch RXEF, 60 VDC, 50 mA, 100 mA, 5 s, Round | 1 | Farnell/Onecall | 1345959
L7805ABV Voltage Regulator, 5V, 7805 | 1 | CPC/Onecall | SC10586
EEUFC1V470 Electrolytic Capacitor, 47 µF, 35 V, ± 20%, Radial Leaded, 1000 hours @ 105°C, Polar | 2 | Farnell/Onecall | 1848447
Qwiic Scale - NAU7802 | 1 | Ebay | https://www.ebay.co.uk/itm/133047867785 | One of NAU7802 or HX711 required, but both can be fitted/trialled if desired
Load Cell Amplifier - HX711 | 1 | Ebay | https://www.ebay.co.uk/itm/132324380365 | One of NAU7802 or HX711 required, but both can be fitted/trialled if desired
SHOTTKEY DIODES
Light source related
CTBP9358/2 5.08mm Horizontal Pluggable Terminal Block Header, 2-Pole, 15A | 2 | CPC/Onecall | CN21009
CTBP9208/2 Pluggable Terminal Block, 5.08 mm, 2 Ways, 28AWG to 14AWG, 1.5 mm², Clamp, 15 A | 10 (MOQ) | Farnell/Onecall | 2527762
1244 10M 2-Core Figure-8 Car Audio Cable 6A 10m | 1 | CPC/Onecall | CB17480
COB LED Panel Light 94x50MM Ultra Bright Strip Lamp 10W COB Board LED *ZY YIUK | 2 | Ebay | https://www.ebay.co.uk/itm/404516299885
5A Lithium Charger CV CC buck Step down Power Supply Module LED Driver XL4015 | 2 | Ebay | https://www.ebay.co.uk/itm/373640284189
Actuator / driver related
LR1LJR10 - Through Hole Resistor, 0.1 ohm, LR, 500 mW, ± 5%, Axial Leaded, 350 V | 10 (MOQ) | Farnell/Onecall | 2330244
1N4002G Standard Recovery Diode, 100 V, 1 A, Single, 1.1 V, 30 A | 5 (MOQ) | CPC/Onecall | SC16432
L298N Dual Full-Bridge Driver 4A Output | 1 | CPC/Onecall | SCL298
SK 686 37,5 SA Heat Sink, 3.6 K/W, 76 mm, 16.8 mm, 37.5 mm | 1 | Farnell/Onecall | 3779066
671-0601 DIN Audio / Video Connector, 6 Contacts, Jack, PCB Mount, Through Hole Right Angle | 1 | Farnell/Onecall | 2989967
590-0600 DIN Audio / Video Connector, Locking, 6 Contacts, Plug, Cable Mount, Solder, Silver Plated Contacts | 1 | Farnell/Onecall | 1193798 | For extension cable (currently not implimented)
C7GBSY Multicore Cable, Per Metre, Screened, 7 Core, 0.75 mm² | 3 | Farnell/Onecall | 2912125 | For extension cable (currently not implimented). Closest suitable screened cable that could be identified
650-0600 6 Pin Panel Socket (DIN) | 1 | CPC/Onecall | CN00076 | For extension cable (currently not implimented)
Interlocking and Estop
590-0400 4 Pin Nickel Locking DIN Plug | 1 | CPC/Onecall | CN00043 | For external interlock microswitches (currently not implimented)
671-0401 DIN Audio / Video Connector, 4 Contacts, Jack, PCB Mount, Through Hole Right Angle | 1 | Farnell/Onecall | 2989965 | For external interlock microswitches (currently not implimented, but used to bridge socket)
A01ES-DM+A0154B-D Emergency Stop Button Switch, DPST-No, 6A, 250V AC | 1 | CPC/Onecall | SW05603
19017-0001 Quick Disconnect Terminal, InsulKrimp 19017, Female Quick Disconnect, 2.8mm x 0.51mm | 4 | Farnell/Onecall | 3049783 | Connectors for estop
CSM30531D Microswitch, V3, Long Wide Lever | 8 | CPC/Onecall | SW03204 | External interlock microswitches (currently not implimented)
2-520193-2 Quick Disconnect Terminal, Ultra-Fast 187, Female Quick Disconnect, 4.75mm x 0.81mm | 20 (multiples of 10) | Farnell/Onecall | 2781647 | Connectors for external interlock microswitches (currently not implimented)
PPSY4C1.00 Multicore Cable, SY, Per M, Screened, 4 Core, 1 mm² | 8 (suggested) | Farnell/Onecall | 1891230 | For external interlock microswitches (currently not implimented)

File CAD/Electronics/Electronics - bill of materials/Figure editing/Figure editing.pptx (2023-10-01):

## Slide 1

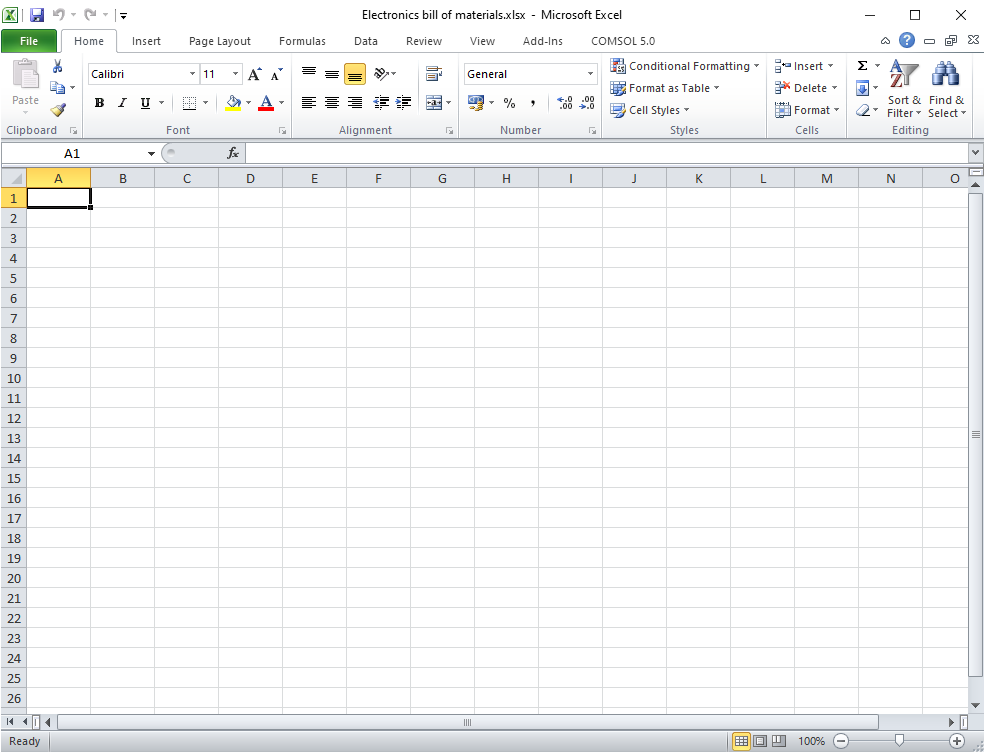
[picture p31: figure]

LINK – CLICK TO OPEN/DOWNLOAD FILE

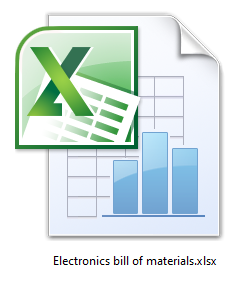
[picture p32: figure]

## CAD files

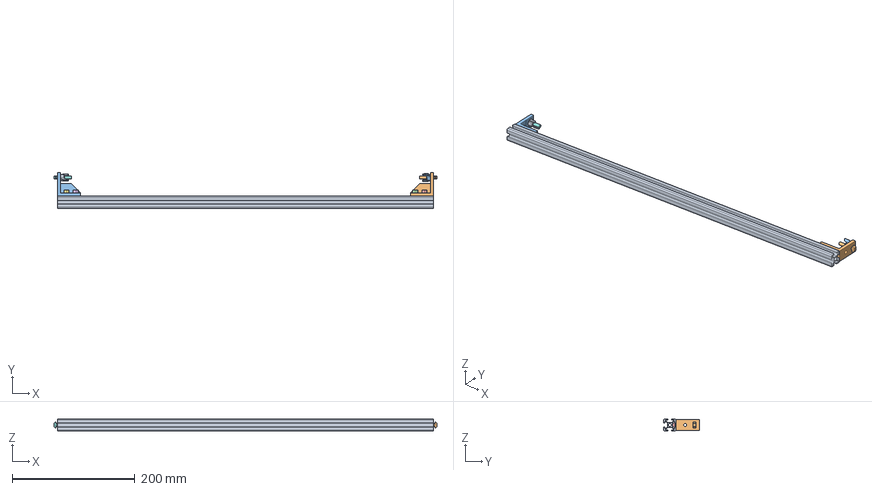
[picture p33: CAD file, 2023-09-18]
CAD/Mechanical/Aluminium rail frame - supporting models/Assembly step 11.FCStd
623.0 x 58.0 x 20.0 mm
2020 Rail 612mm long_001
2040 Right angle bracket approximate outline - cutout A_001
2040 Right angle bracket approximate outline - cutout B_001
Assembly M5x10MM Cap head rail nut 5mm object_001
Assembly M5x10MM Cap head rail nut 5mm object_002
Assembly M5x10MM Cap head rail nut 5mm object_003
Assembly M5x10MM Cap head rail nut 5mm object_004
2020 Drop in T bolt M5 25mm_001
Assembly M5 wing nut trimmed wings_001
2020 Drop in T bolt M5 25mm_002
Assembly M5 wing nut trimmed wings_002

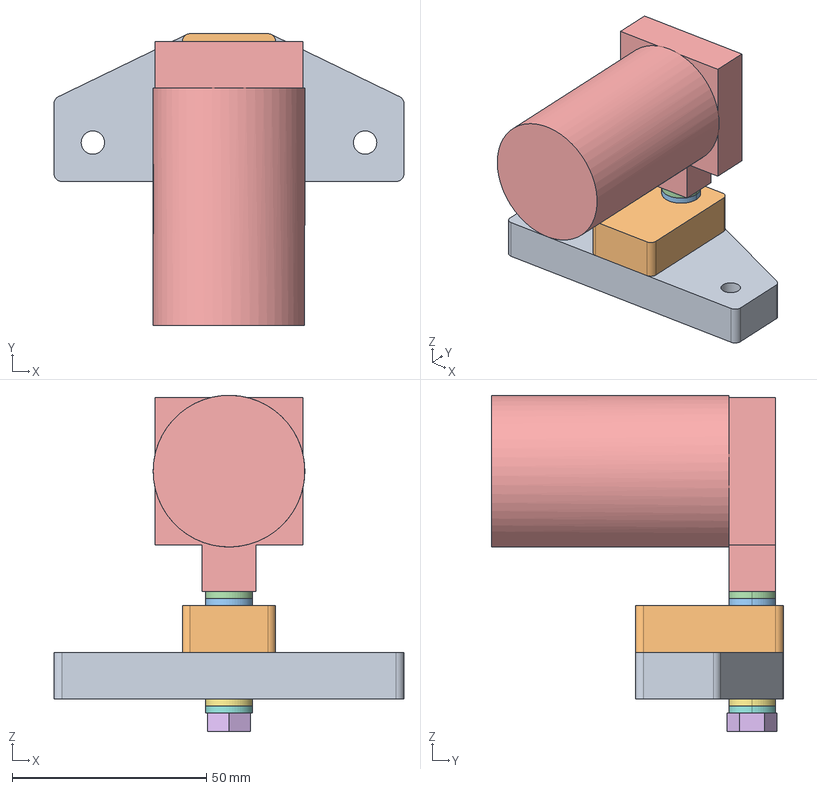
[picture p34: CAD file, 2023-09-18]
CAD/Mechanical/Camera and light fittings - supporting models/Assembly camera on bracket.FCStd
90.0 x 75.0 x 86.5 mm
V2 Camera mount plate_001
V2 Camera spacer plate_001
TR Fastenings Ltd-M6 Flat Washer to DIN125A1_001
TR Fastenings Ltd-M6 Flat Washer to DIN125A1_002
Camera mock up Pi HQ camera and telephoto lens_001
0_25 inch UNC x 1_5 inch Hex head_001
TR Fastenings Ltd-M6 Flat Washer to DIN125A1_003
TR Fastenings Ltd-M6 Flat Washer to DIN125A1_004

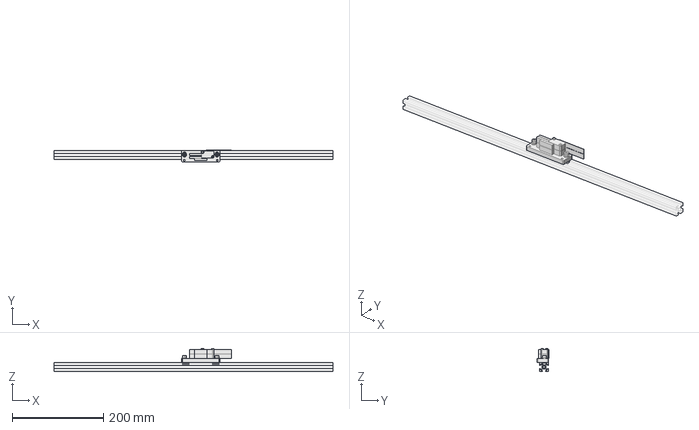
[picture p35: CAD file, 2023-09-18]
CAD/Mechanical/Doors - supporting models/Assembly mounted microswitch on example rail.FCStd
610.0 x 26.5 x 50.4 mm
Assembly microswitch on bracket_001
2020 Rail 610mm long_001

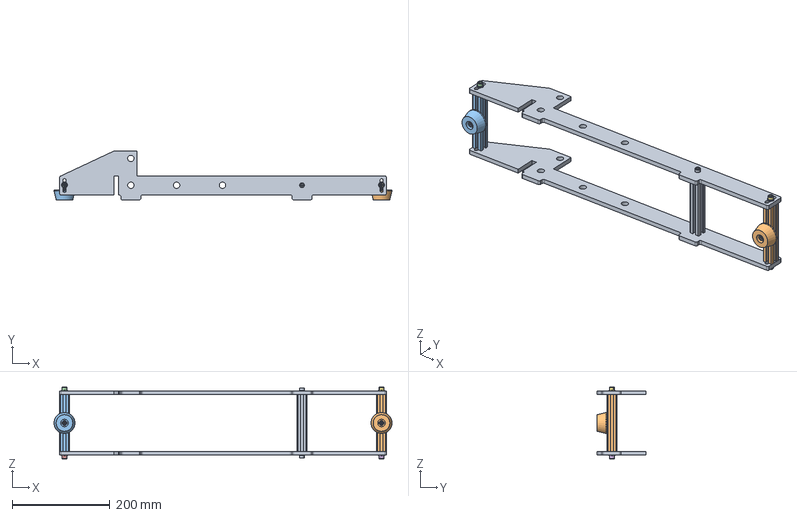
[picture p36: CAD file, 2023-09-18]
CAD/Mechanical/Feet - supporting models/Assembly step 4.FCStd
693.0 x 100.0 x 147.6 mm
Assembly step 3_001
Assembly step 1_001
Assembly step 1_002
Assembly M6x25MM Cap head with washer_001
Assembly M6x25MM Cap head with washer_002
Assembly M6x25MM Cap head with washer_003
Assembly M6x25MM Cap head with washer_004

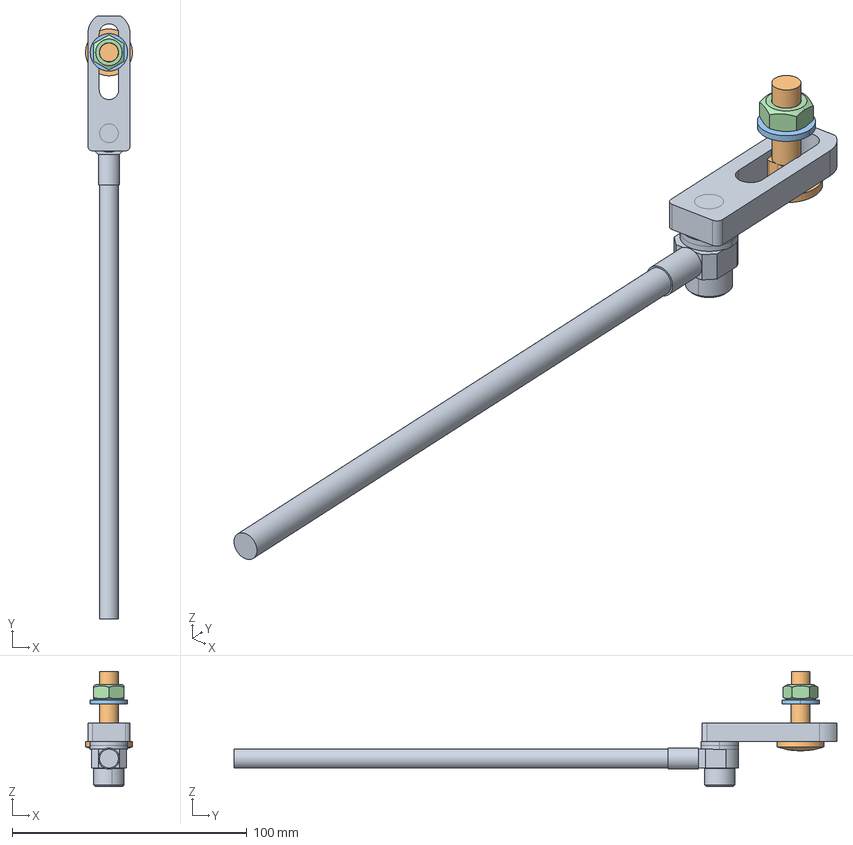
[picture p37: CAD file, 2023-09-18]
CAD/Mechanical/Gas spring - supporting models/Assembly gas strut rod mounted.FCStd
20.0 x 257.0 x 49.2 mm
Assembly gas strut rod_001
M8 Coach bolt_001
TR Fastenings Ltd-M8 Flat Washer to DIN125A1_001
TR Fastenings Ltd-M8 Hexagon Full Nut to DIN 934 ~ISO 40321_001

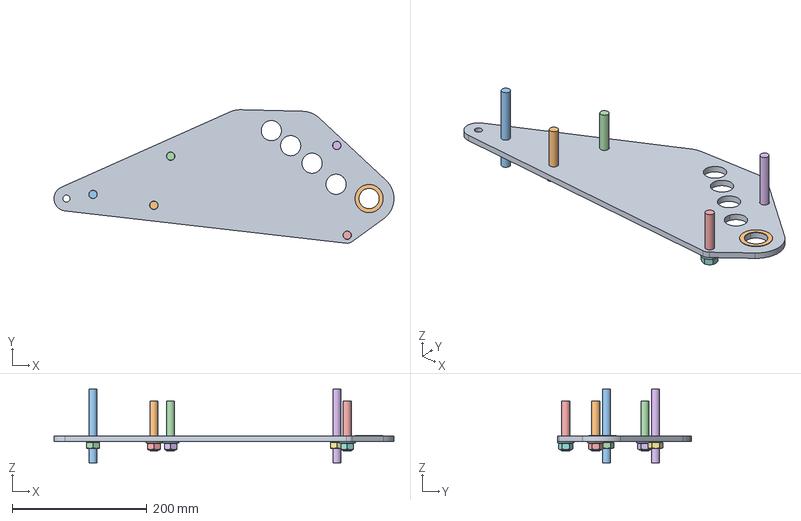
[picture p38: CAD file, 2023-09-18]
CAD/Mechanical/Lever - supporting models/Assembly lever static parts step 1.FCStd
505.5 x 198.6 x 110.0 mm
V2 Lever arm FEA_001
M12x74MM threaded rod_001
M12x110MM threaded rod_001
M12x74MM threaded rod_002
M12x74MM threaded rod_003
M12x110MM threaded rod_002
Assembly TR Fastenings Ltd-M12 Internal Toothed Washer DIN 6797J_001
Assembly TR Fastenings Ltd-M12 Internal Toothed Washer DIN 6797J_002
TR Fastenings Ltd-M12 Flat Washer to DIN125A1_001
TR Fastenings Ltd-M12 Flat Washer to DIN125A1_002
TR Fastenings Ltd-M12 Flat Washer to DIN125A1_003
TR Fastenings Ltd-M12 Hexagon Full Nut to DIN 9341_001
TR Fastenings Ltd-M12 Hexagon Full Nut to DIN 9341_002
TR Fastenings Ltd-M12 Hexagon Full Nut to DIN 9341_003
TR Fastenings Ltd-M12 Hexagon Full Nut to DIN 9341_004
TR Fastenings Ltd-M12 Hexagon Full Nut to DIN 9341_005
30 x 42 x 0_3mm shim washer_001
30 x 42 x 0_3mm shim washer_002

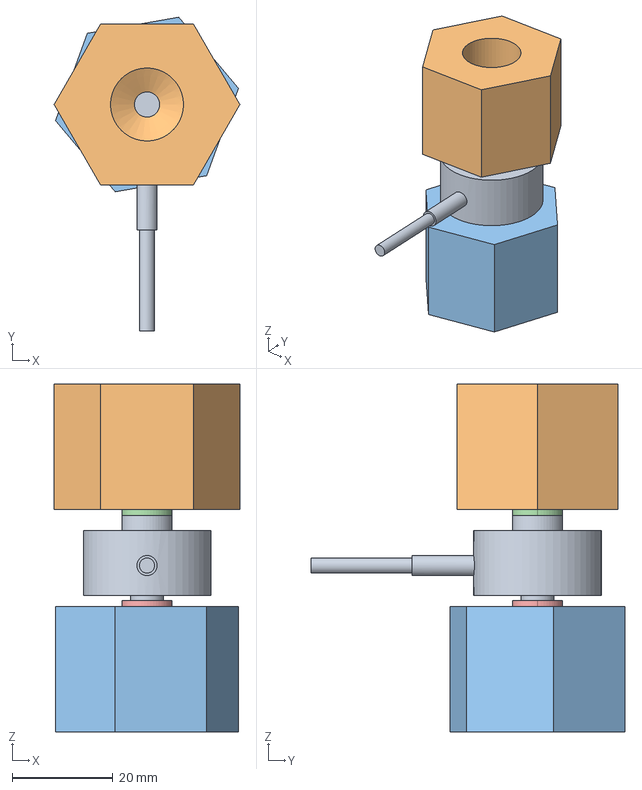
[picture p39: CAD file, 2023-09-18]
CAD/Mechanical/Load cell and clamp mounting - supporting models/Assembly step 3B.FCStd
37.0 x 62.4 x 69.2 mm
50kg load cell_001
V2 Thread adapter blank low load_001
V2 Thread adapter blank low load_002
TR Fastenings Ltd-M5 Flat Washer to DIN125A1_001
TR Fastenings Ltd-M5 Flat Washer to DIN125A1_002

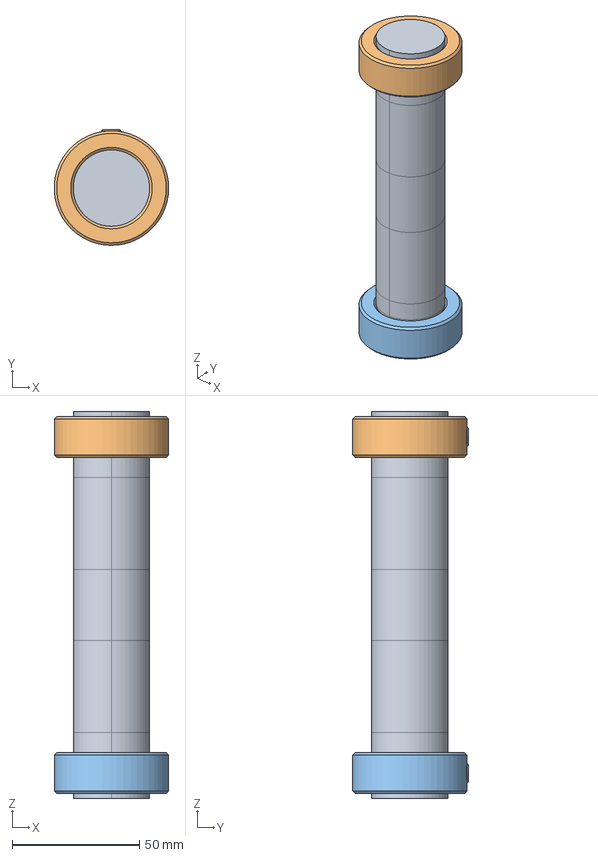
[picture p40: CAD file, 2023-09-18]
CAD/Mechanical/Pins and collars - supporting models/Assembly pivot-frame pin with collars.FCStd
45.0 x 45.5 x 152.0 mm
30mm diameter 152mm long pivot-frame pin FEA_001
Assembly shaft collar 30mm_001
Assembly shaft collar 30mm_002

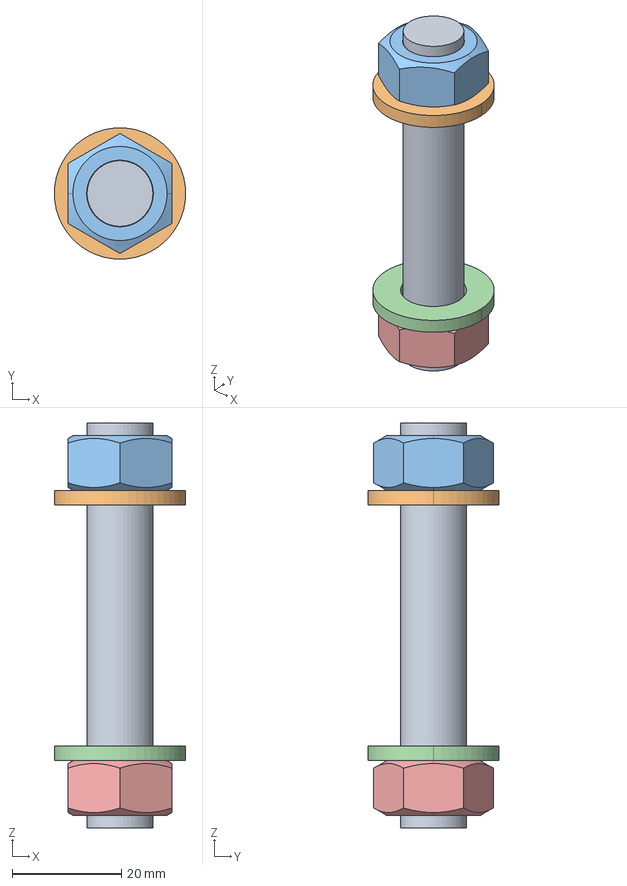
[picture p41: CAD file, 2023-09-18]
CAD/Mechanical/Pivot parts and guides - supporting models/Assembly pivot arm long stud.FCStd
24.0 x 24.0 x 74.0 mm
M12x74MM threaded rod_001
TR Fastenings Ltd-M12 Flat Washer to DIN125A1_001
TR Fastenings Ltd-M12 Hexagon Full Nut to DIN 9341_001
TR Fastenings Ltd-M12 Flat Washer to DIN125A1_002
TR Fastenings Ltd-M12 Hexagon Full Nut to DIN 9341_002

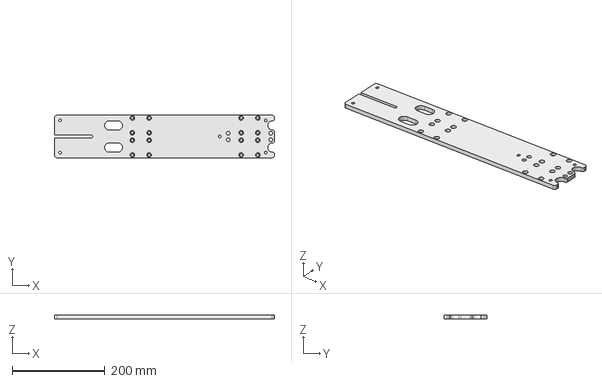
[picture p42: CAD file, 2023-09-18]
CAD/Mechanical/Slider assembly - part designs/V2 Coupling plate sliding assembly.FCStd
475.0 x 92.0 x 8.00 mm

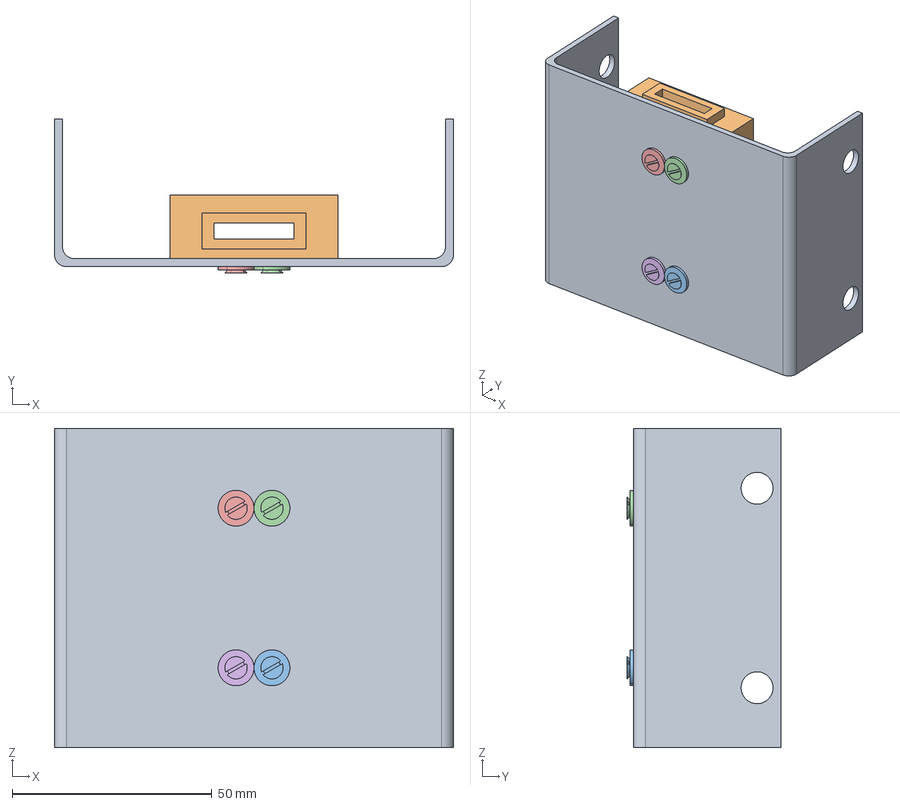
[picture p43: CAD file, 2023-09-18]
CAD/Mechanical/Slider assembly - supporting models/Assembly linear scale body and bracket.FCStd
100.0 x 38.6 x 80.0 mm
Linear scale mounting bracket_001
Linear scale body_001
Assembly M3 for linear scale mounting_001
Assembly M3 for linear scale mounting_002
Assembly M3 for linear scale mounting_003
Assembly M3 for linear scale mounting_004

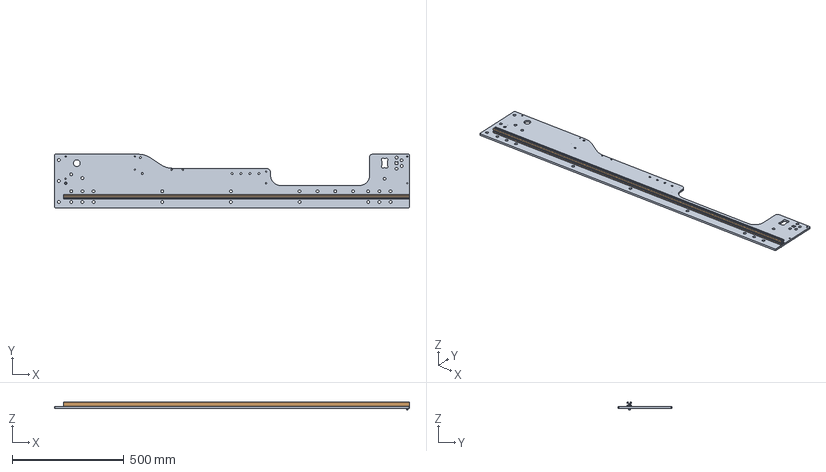
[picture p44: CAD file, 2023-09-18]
CAD/Mechanical/Superstructure - supporting models/Assembly step 1 right plate.FCStd
1590.0 x 240.0 x 35.2 mm
V2 Side mounting plate + right plate countersinks_001
2020 Rail 1550mm long_001
Assembly M5x16MM Cap head rail nut 8mm object_001
Assembly M5x12MM Countersunk head rail nut 6-8mm object_001
Assembly M5x12MM Countersunk head rail nut 6-8mm object_002
Assembly M5x12MM Countersunk head rail nut 6-8mm object_003
Assembly M5x12MM Countersunk head rail nut 6-8mm object_004
Assembly M5x12MM Countersunk head rail nut 6-8mm object_005
Assembly M5x12MM Countersunk head rail nut 6-8mm object_006

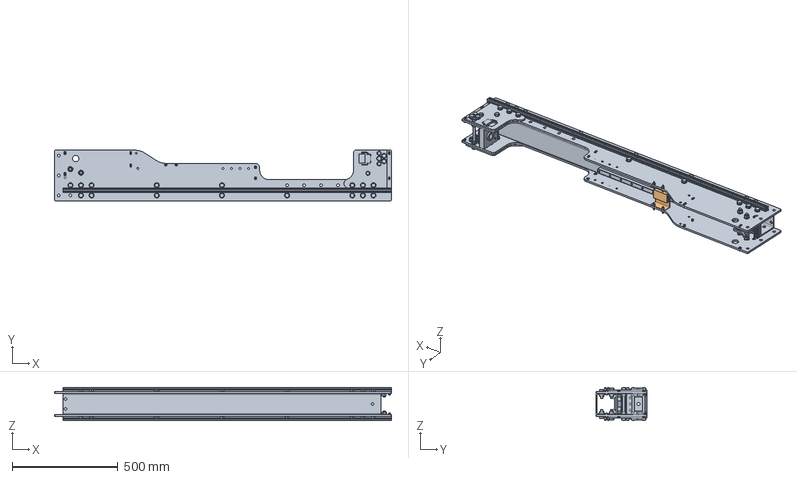
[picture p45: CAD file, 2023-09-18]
CAD/Mechanical/Superstructure rail frame and feet attachment - supporting models/Assembly static parts step 1.FCStd
1590.0 x 240.0 x 156.0 mm
Assembly step 10_001
Assembly M5x16MM Cap head rail nut 8mm object_001
Assembly M5x16MM Cap head rail nut 8mm object_002
Assembly M5x16MM Cap head rail nut 8mm object_003
Assembly M5x16MM Cap head rail nut 8mm object_004
Assembly M5x12MM Countersunk head rail nut 6-8mm object_001
Assembly M5x12MM Countersunk head rail nut 6-8mm object_002
Assembly M5x12MM Countersunk head rail nut 6-8mm object_003
Assembly M5x12MM Countersunk head rail nut 6-8mm object_004
Assembly M5x12MM Countersunk head rail nut 6-8mm object_005
Assembly M5x12MM Countersunk head rail nut 6-8mm object_006
Assembly M5x12MM Countersunk head rail nut 6-8mm object_007
Assembly M5x12MM Countersunk head rail nut 6-8mm object_008
Assembly M5x16MM Cap head rail nut 8mm object_005
Assembly M5x16MM Cap head rail nut 8mm object_006
Assembly M5x16MM Cap head rail nut 8mm object_007
Assembly M5x16MM Cap head rail nut 8mm object_008
Assembly linear scale body and bracket with bolts_001

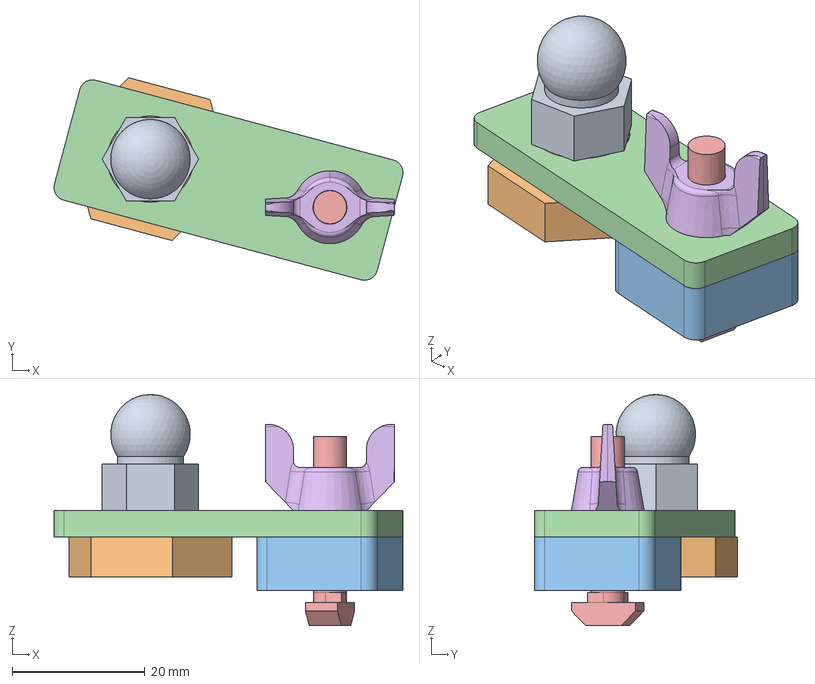
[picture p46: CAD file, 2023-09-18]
CAD/Mechanical/Camera and light fittings - supporting models/Assembly flexible coolant pipe on bracket.FCStd
52.6 x 30.5 x 34.8 mm
Flexible coolant pipe base_001
Flexible coolant pipe nut_001
V2 Flexible coolant pipe mount for LEDs spacer_001
V2 Flexible coolant pipe mount for LEDs_001
2020 Drop in T bolt M5 25mm_001
Assembly M5 wing nut trimmed wings_001

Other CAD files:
CAD/Mechanical/Feet - supporting models/Assembly step 5.FCStd
CAD/Mechanical/Gas spring - supporting models/Assembly step 1 and 2.FCStd
CAD/Mechanical/Lever - supporting models/Assembly lever static parts step 3.FCStd
CAD/Mechanical/Pivot parts and guides - supporting models/Assembly pivot with actuator frame and range pins.FCStd
CAD/Mechanical/Aluminium rail frame - part designs/V2 Enclosure ends U bracket with rail end holes.FCStd
CAD/Mechanical/Aluminium rail frame - part designs/V2 Enclosure ends U bracket with rail end holes.dxf
CAD/Mechanical/Aluminium rail frame - part designs/V2 Enclosure ends U bracket without rail end holes.FCStd
CAD/Mechanical/Aluminium rail frame - part designs/V2 Enclosure ends U bracket without rail end holes.dxf
CAD/Mechanical/Aluminium rail frame - part designs/V2 Enclosure ends right angle bracket.FCStd
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

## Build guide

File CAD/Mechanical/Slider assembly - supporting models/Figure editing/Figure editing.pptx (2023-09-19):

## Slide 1

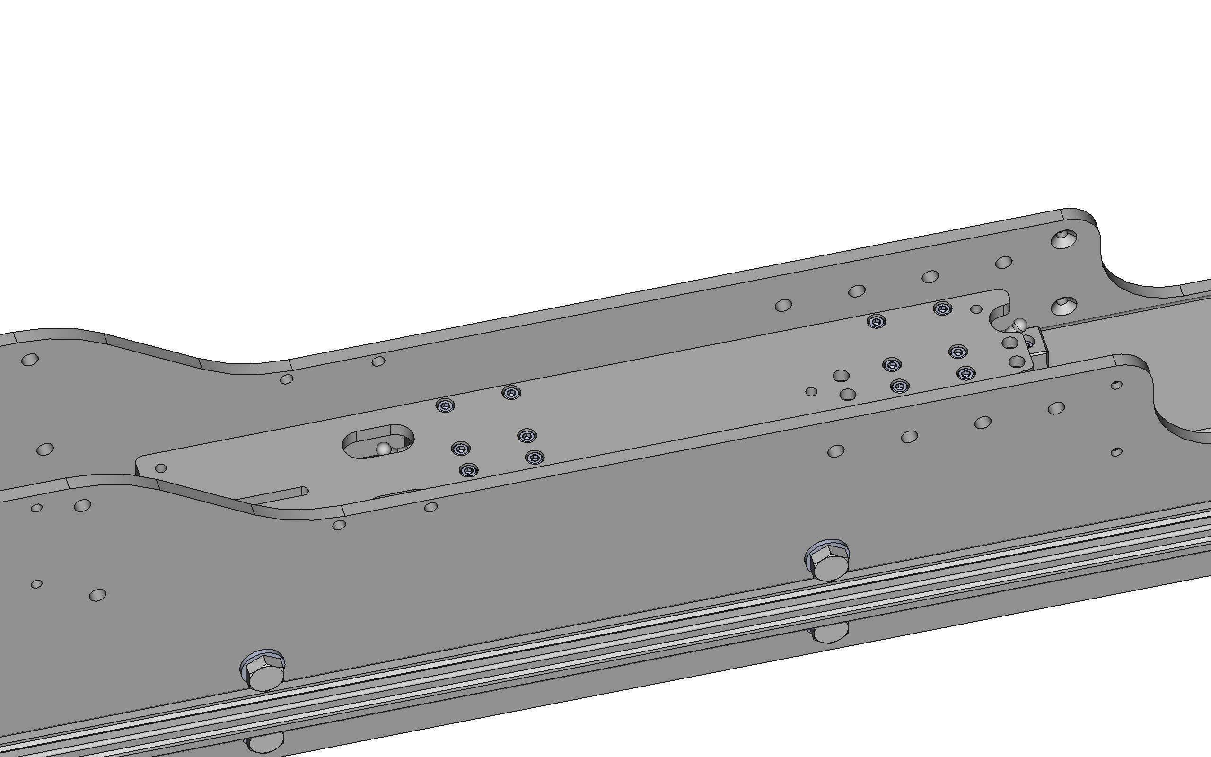
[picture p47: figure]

First loosely fit coupling plate to carriages
Then use a dial test indicator attached to instrument frame and probe against an edge of coupling plate (whilst sliding the coupling plate) to align it parallel to the rails, before tightening screws

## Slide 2

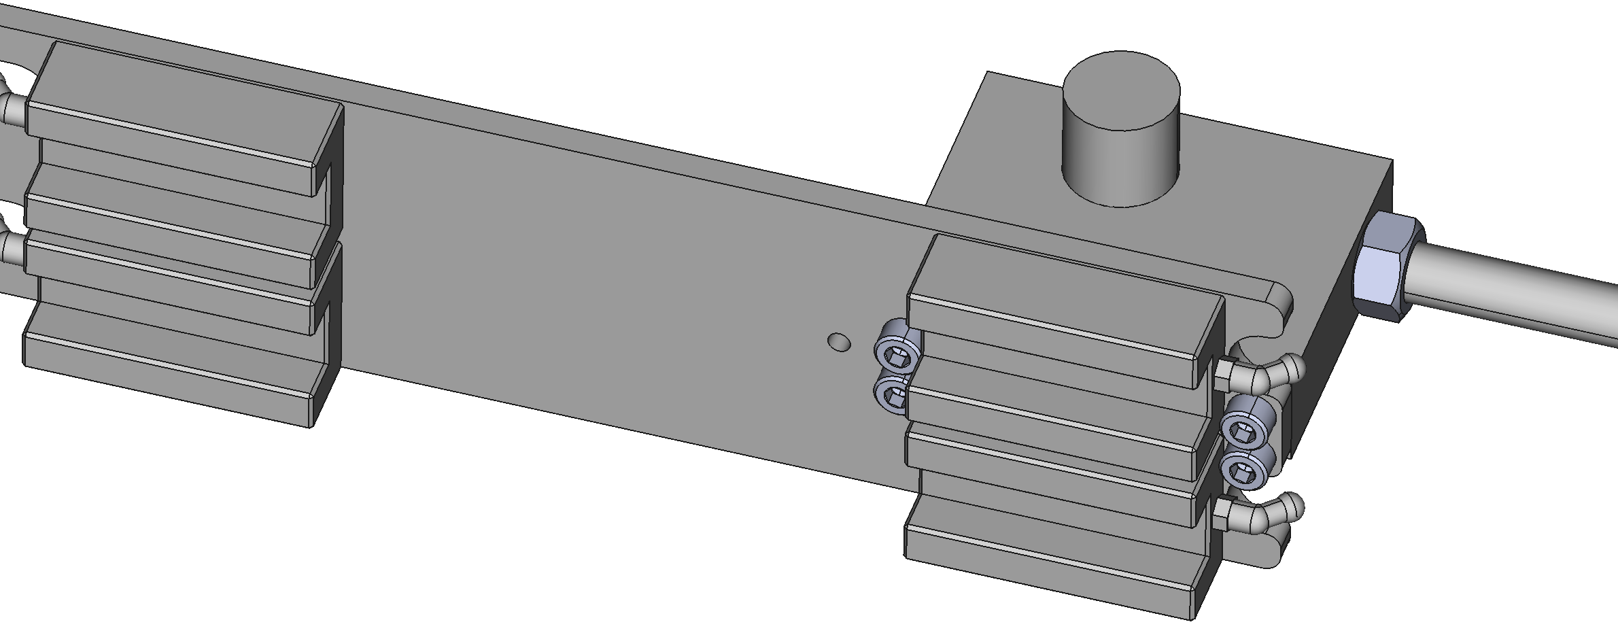
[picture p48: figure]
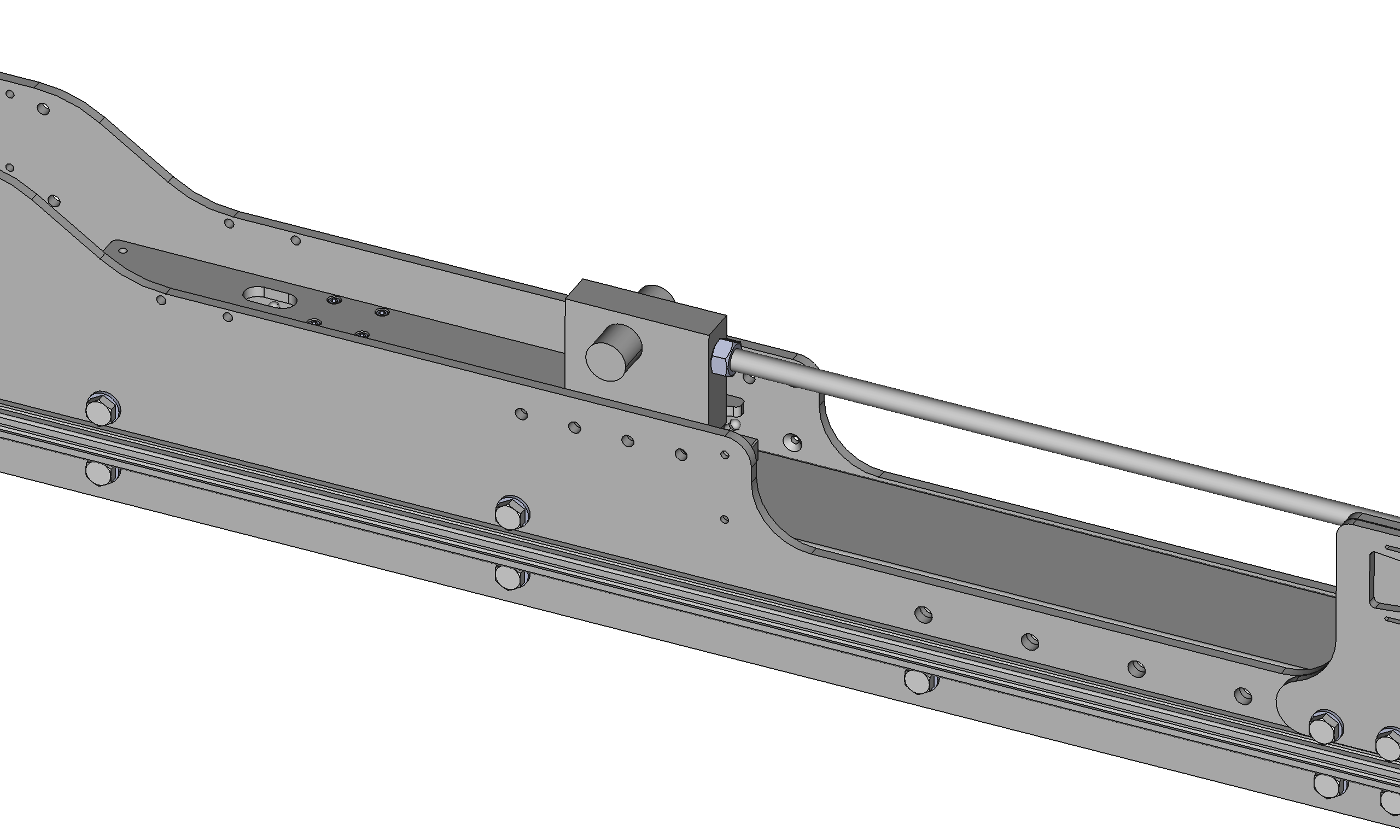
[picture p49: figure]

Then use dial test indicator attached to instrument frame, probing against threaded bar, to rotationally align coupling block by gently tapping the bar, before gently removing the assembly and tightening mounting screws

First fit threaded bar and loosely attach coupling block with associated mounting screws

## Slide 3

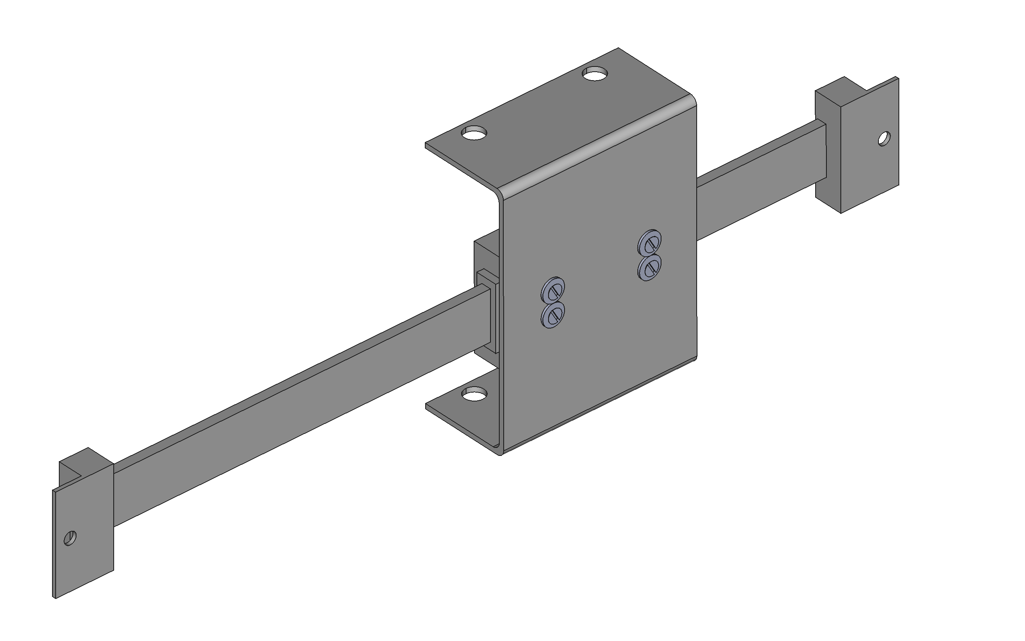
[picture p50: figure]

Linear scale body attached with M3 countersunk screws and M4 washers to bracket

Align rail parallel to sides of mounting bracket and centred across bracket – check squareness and centring using opposite side of mounting bracket (folded bracket may not be precisely square)

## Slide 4

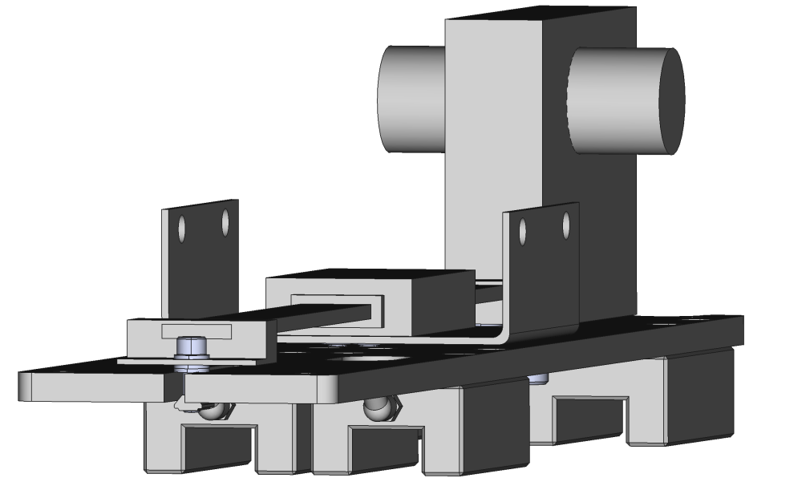
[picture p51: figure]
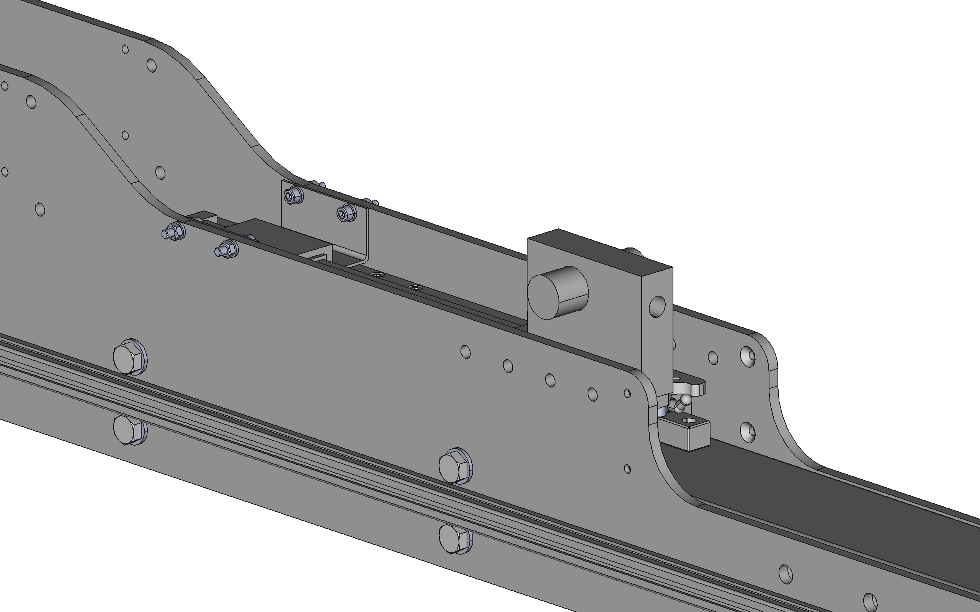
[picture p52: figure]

Linear scale bracket attaches using holes in instrument side plates

Linear scale rail spaced by ~2x M5 washers at both ends. Rail nut used in slotted plate end, opposite end is a tapped hole

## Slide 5

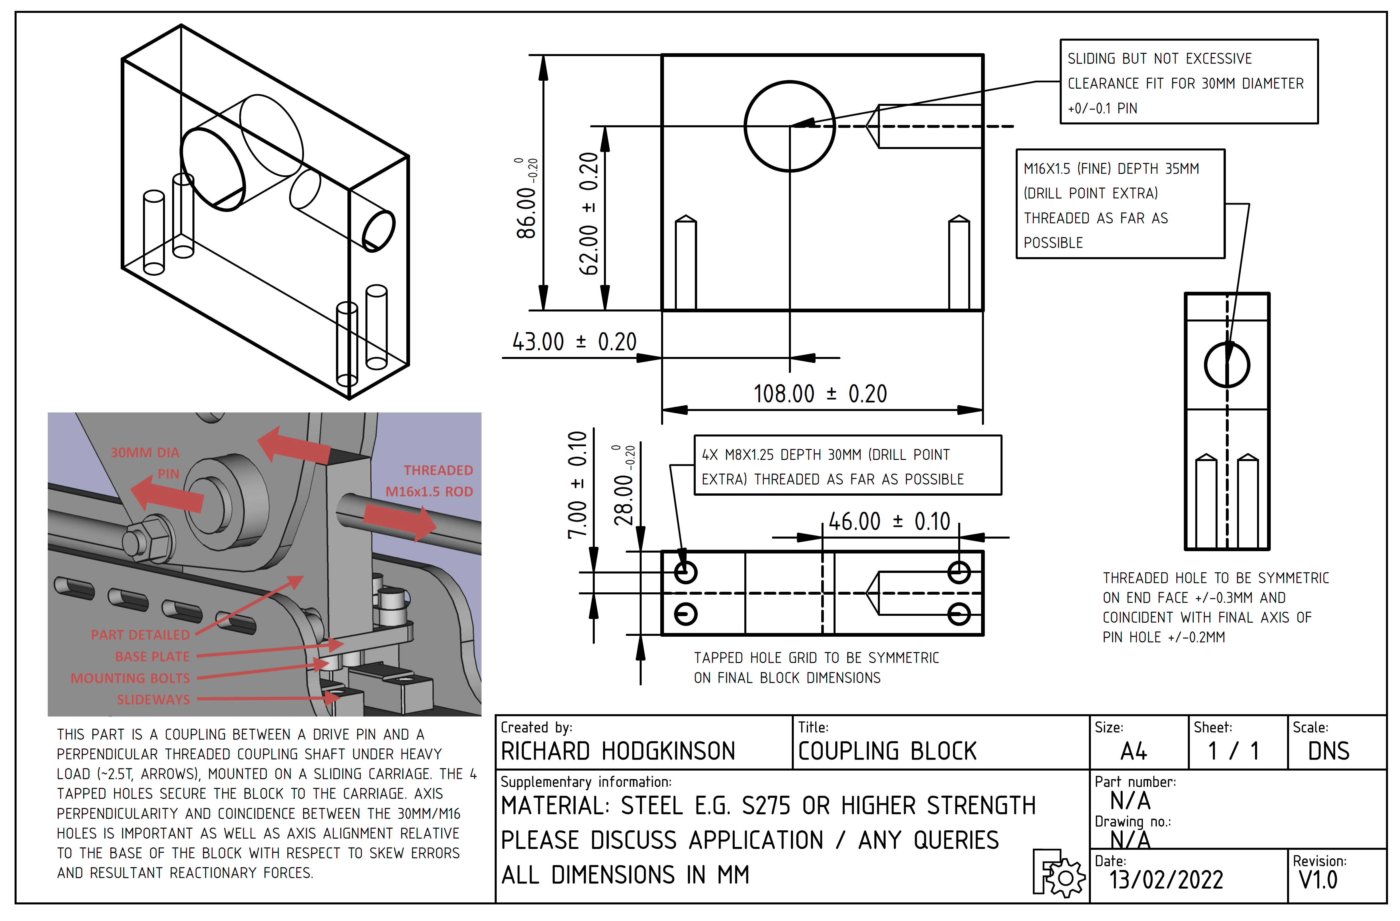
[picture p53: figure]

LINK – CLICK TO OPEN/DOWNLOAD FILE

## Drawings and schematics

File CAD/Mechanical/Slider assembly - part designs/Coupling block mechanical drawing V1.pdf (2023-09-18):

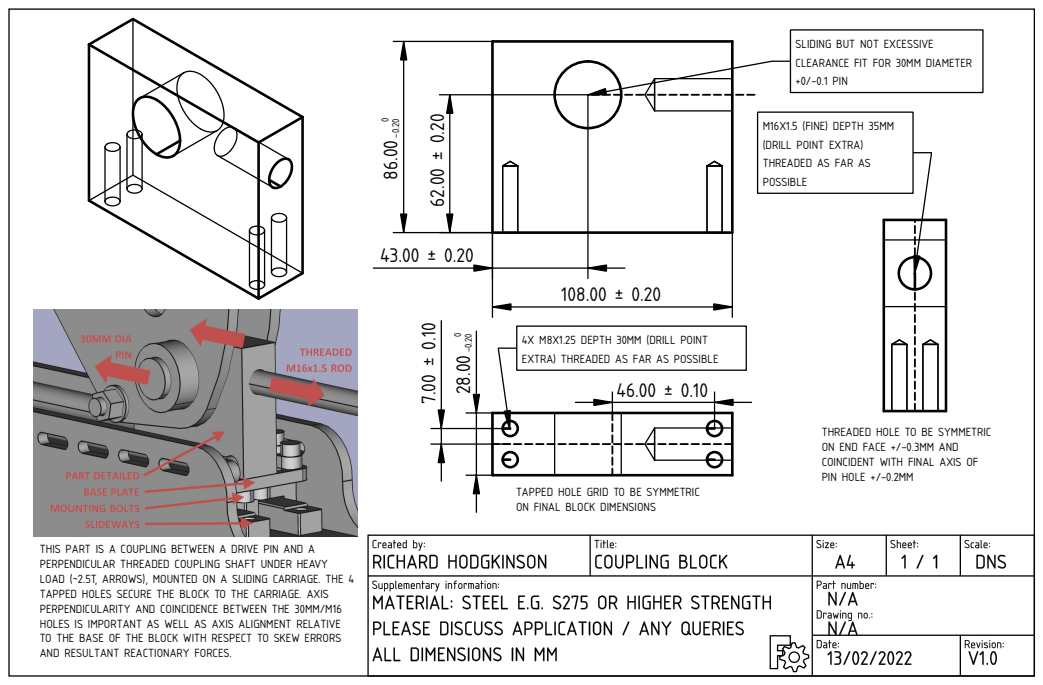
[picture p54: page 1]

SLIDING BUT NOT EXCESSIVE
CLEARANCE FIT FOR 30MM DIAMETER
+0/-0.1 PIN

M16X1.5 (FINE) DEPTH 35MM
(DRILL POINT EXTRA)
THREADED AS FAR AS
POSSIBLE

4X M8X1.25 DEPTH 30MM (DRILL POINT
EXTRA) THREADED AS FAR AS POSSIBLE

THREADED HOLE TO BE SYMMETRIC
ON END FACE +/-0.3MM AND
COINCIDENT WITH FINAL AXIS OF
PIN HOLE +/-0.2MM

TAPPED HOLE GRID TO BE SYMMETRIC
ON FINAL BLOCK DIMENSIONS

THIS PART IS A COUPLING BETWEEN A DRIVE PIN AND A
PERPENDICULAR THREADED COUPLING SHAFT UNDER HEAVY
LOAD (~2.5T, ARROWS), MOUNTED ON A SLIDING CARRIAGE. THE 4
TAPPED HOLES SECURE THE BLOCK TO THE CARRIAGE. AXIS
PERPENDICULARITY AND COINCIDENCE BETWEEN THE 30MM/M16
HOLES IS IMPORTANT AS WELL AS AXIS ALIGNMENT RELATIVE
TO THE BASE OF THE BLOCK WITH RESPECT TO SKEW ERRORS
AND RESULTANT REACTIONARY FORCES.

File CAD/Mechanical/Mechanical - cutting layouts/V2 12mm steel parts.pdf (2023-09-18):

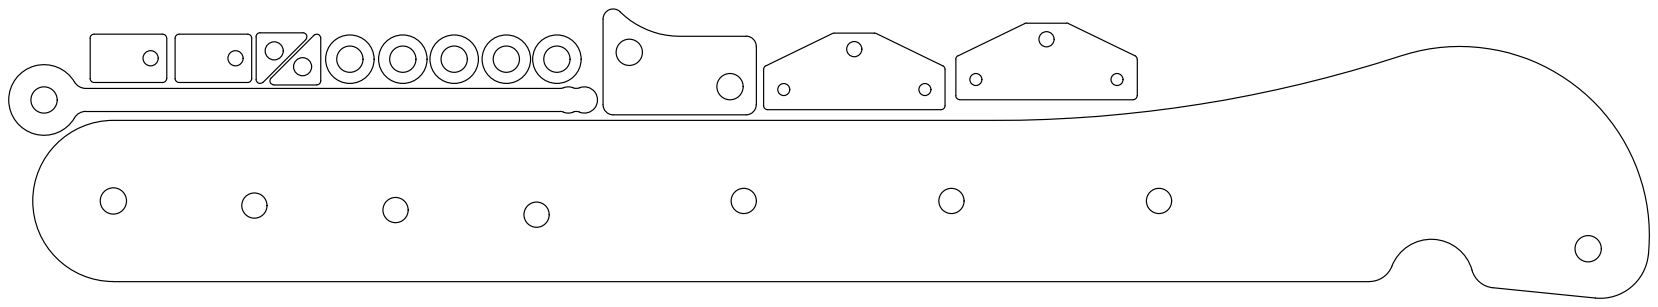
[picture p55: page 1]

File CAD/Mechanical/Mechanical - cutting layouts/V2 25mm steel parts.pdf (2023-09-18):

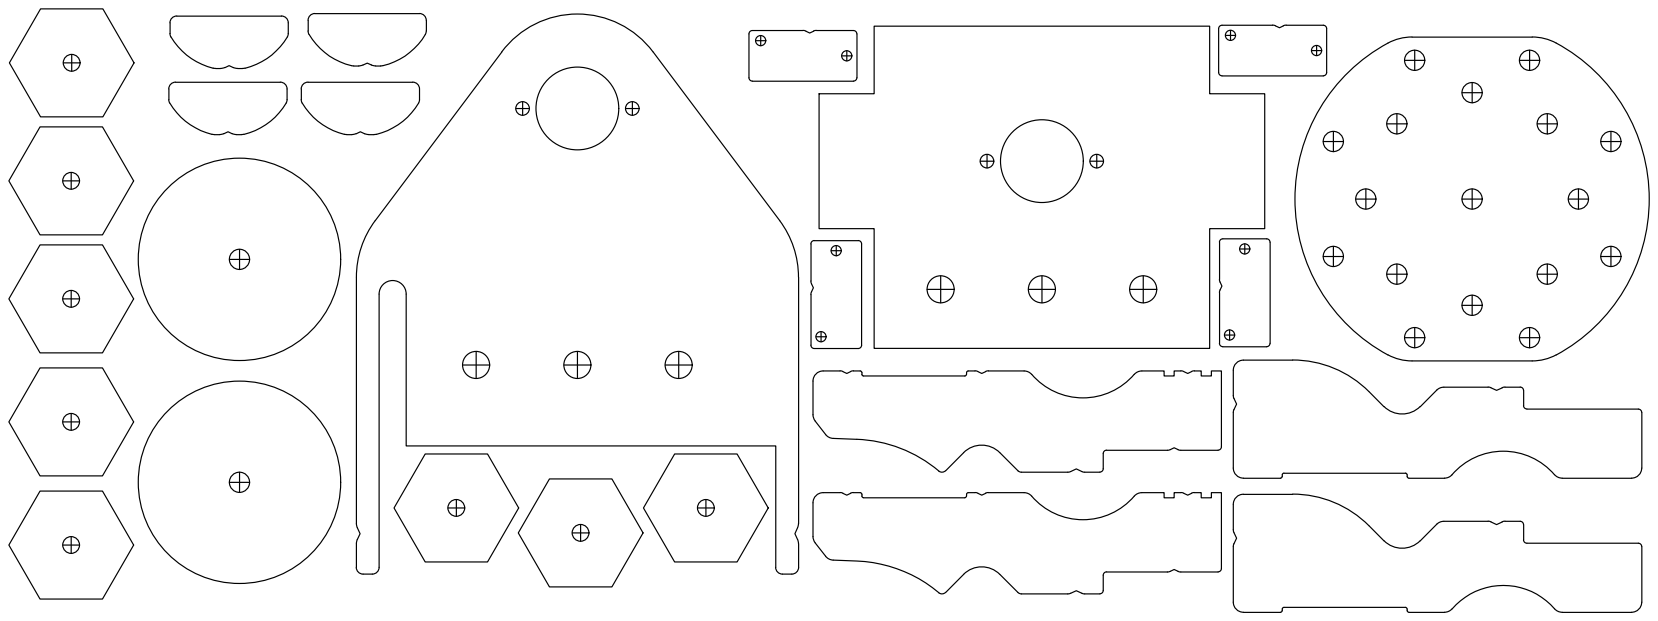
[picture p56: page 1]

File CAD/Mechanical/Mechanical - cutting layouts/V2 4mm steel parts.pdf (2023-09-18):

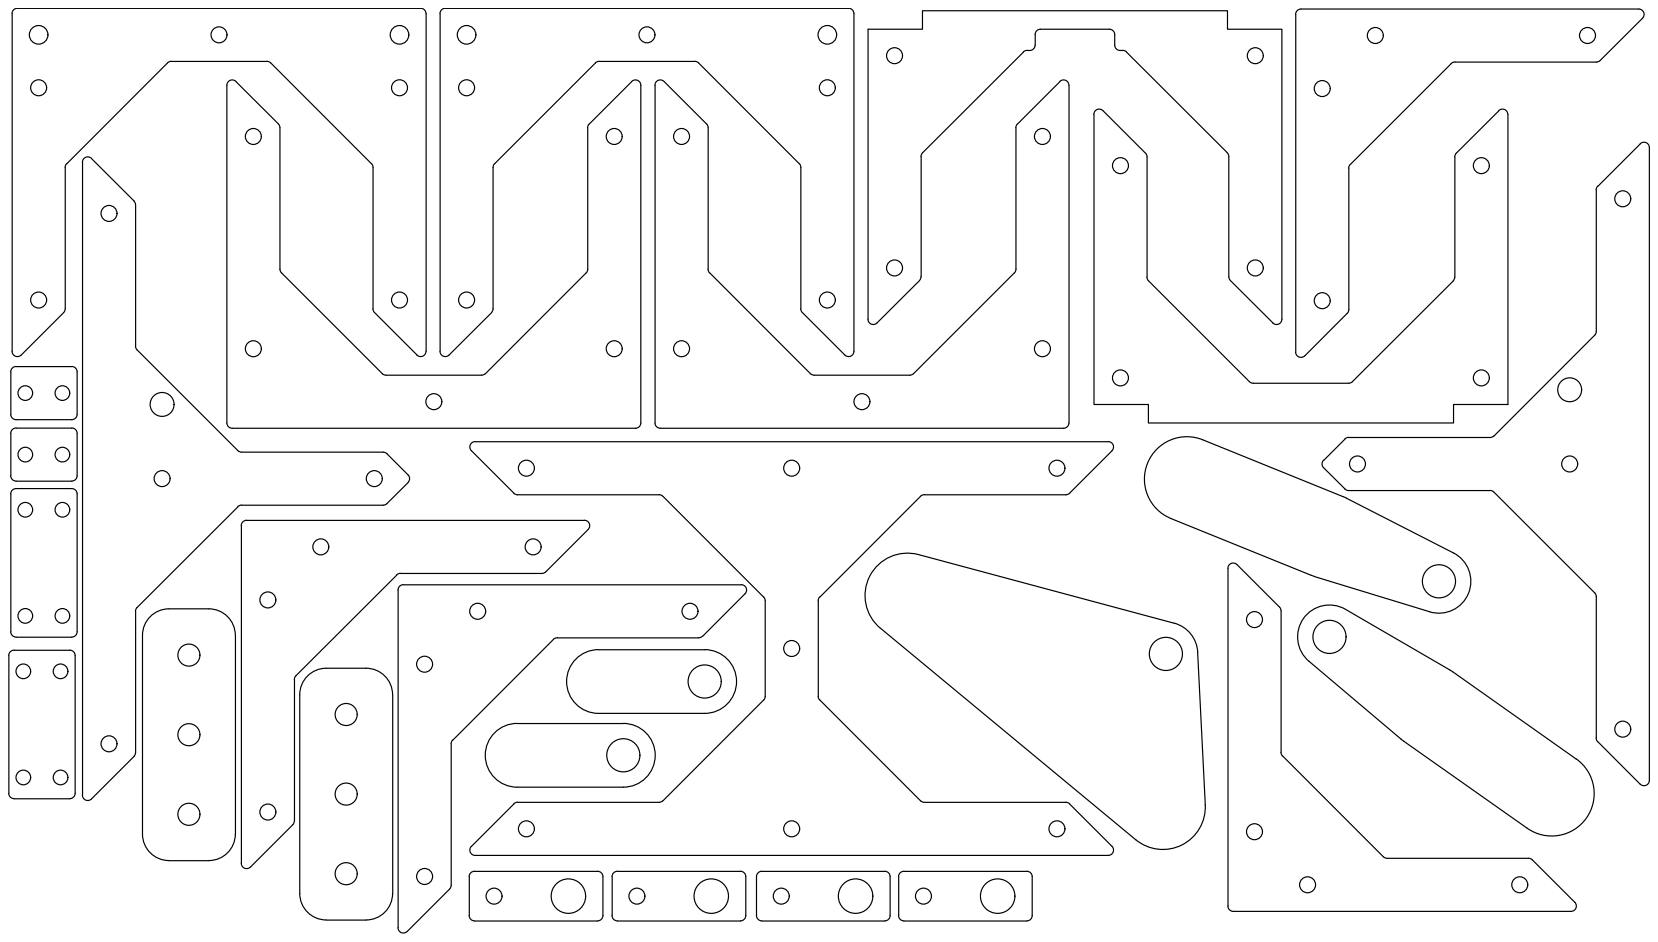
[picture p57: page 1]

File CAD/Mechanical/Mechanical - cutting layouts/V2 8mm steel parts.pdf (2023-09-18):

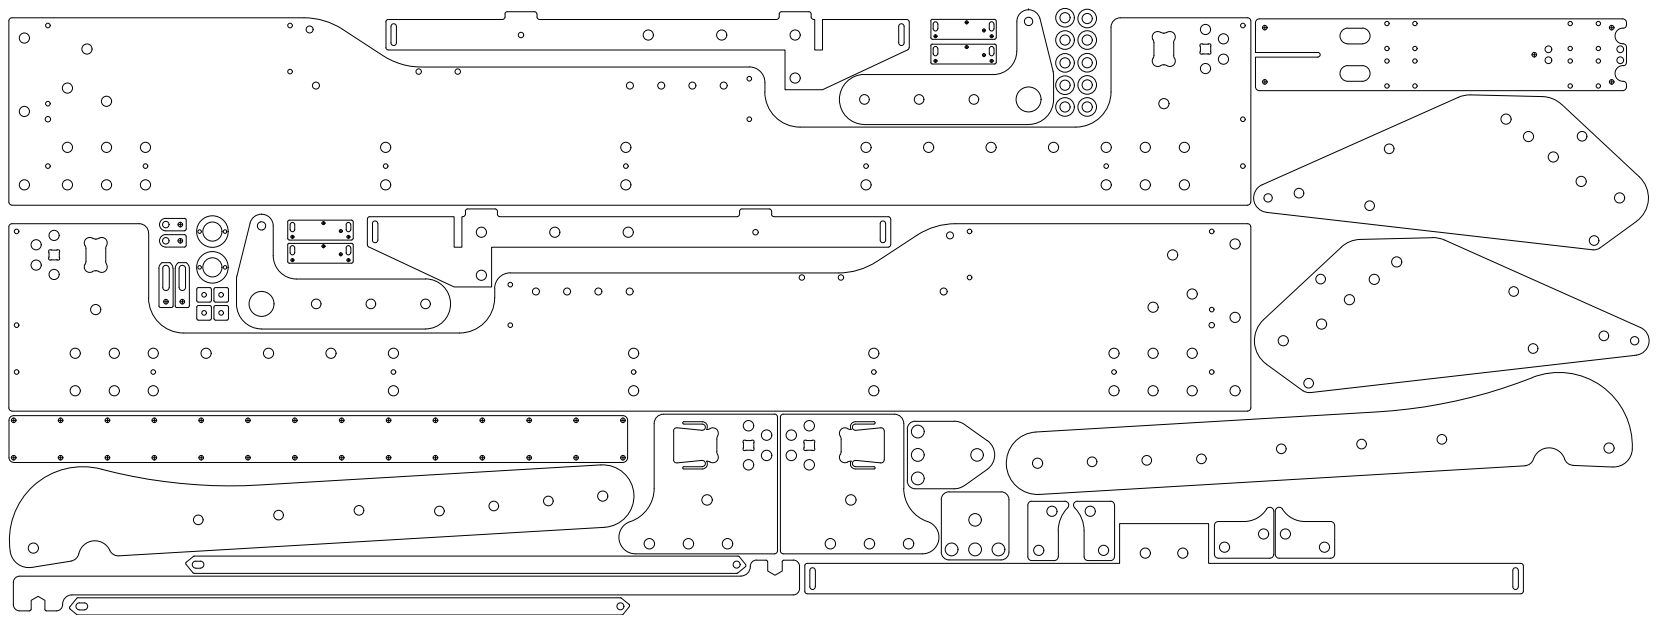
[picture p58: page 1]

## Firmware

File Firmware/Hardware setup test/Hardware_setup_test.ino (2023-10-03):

int actuatorFwd = 19;
int actuatorRev = 18;
int actuatorPWM = 10;
int LED1PWM = 5;
int LED2PWM = 9;
int level=0;
int waitloop1=5;   // retract actuator
int waitloop2=5;  // extend actuator

void setup() {
  // put your setup code here, to run once:
pinMode(actuatorFwd,OUTPUT);
pinMode(actuatorRev,OUTPUT);
pinMode(actuatorPWM,OUTPUT);
pinMode(LED1PWM,OUTPUT);
pinMode(LED2PWM,OUTPUT);
}

void loop() {
  // put your main code here, to run repeatedly:
  digitalWrite(actuatorFwd,1);
  digitalWrite(actuatorRev,0);

  
  for (level=0; level < 255; level++) {
    analogWrite(actuatorPWM, level);
    analogWrite(LED1PWM, level);   
    delay(waitloop1);
  }
  for (level=255; level > 0; level--) {
    analogWrite(actuatorPWM, level);
    analogWrite(LED1PWM, level);   
    delay(waitloop1);
  }
   
  digitalWrite(actuatorFwd,0);
  digitalWrite(actuatorRev,1);
  
  for (; level < 255; level++) {
    analogWrite(actuatorPWM, level);
    analogWrite(LED2PWM, level);   
    delay(waitloop2);
  }
  for (; level > 0; level--) {
    analogWrite(actuatorPWM, level);
    analogWrite(LED2PWM, level);   
    delay(waitloop2);
  }
}

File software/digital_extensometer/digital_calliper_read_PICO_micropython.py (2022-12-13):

from machine import Pin
import time
import micropython
micropython.alloc_emergency_exception_buf(100)

def decode(Pin):           #defining interrupt handling function
    global position
    global idx
    global current_position
    global t_last_bit
    global reading_start
    global t_current_bit
    global velocity
    global bitArray
    
   
    data_value = data.value()
    t_current_bit = time.ticks_us()
    delta = t_current_bit - t_last_bit
    t_last_bit = t_current_bit
    #print(idx, delta, data_value, position)
   
    
    if delta > 5000 or idx > 23:
        # We have reached the end of the position clock bits OR position is unfeasibly large
        # RESET everything
        idx = 0
        position = 0
        bitArray = []
    
    
    if idx < 20 : # For the first 20 clock pulses 
        if data_value == 1: # If the data bit is high do this
            position += 2**idx # Add the next positive bit to the position
            #bitArray.append(1)
            
        #else:
            #bitArray.append(0)

            
            
    elif idx == 20: # This is the 'sign' clock pulse
        if data_value == 1: # If the data bit is positive here it means the calliper position should be negative
            position = -1 * position # Make the position negative
            #bitArray.append(1)
        #else:
            #bitArray.append(0)
    
    elif idx == 23: # 24th bit is the last on in the sequence
        delta_t = reading_start - t_last_bit
        position = position*10 # Send position in microns
        delta_d = current_position - position
        velocity = int(abs(delta_d*1e6/delta_t)) # Velocity in microns per second
        #print(bitArray)
        print(f"{position} {velocity}") # Print out the position, formatted to 2 decimel places as per the calliper LCD read out
        current_position = position
        reading_start = t_current_bit
    
    
    idx += 1
        



led = Pin(17, Pin.OUT)
data = Pin(3, Pin.IN) # Initialise the data pin (GP3 on the Pico, pin 5 on the pinout map)
data_out = Pin(26, Pin.OUT)
idx = 0 # Initialise the bit index
position = 0 # Initialise the position
velocity = 0
interrupt = Pin(2,Pin.IN)   # setting GP2 PIR_Interrupt as input
interrupt.irq( trigger = Pin.IRQ_RISING, handler = decode) # Define the interrupt to only occur on the rising edge of the clock line     

t_last_bit = time.ticks_us()
reading_start = 0
t_current_bit= 0
current_position = 0.0
delay = 0.5
bitArray = []

while True:
    pass
    
    
        
        
        
        
        
        

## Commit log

2023-01-04 Create aluminium rail frame - part designs
2023-05-07 Create clamps and fixtures - part designs
